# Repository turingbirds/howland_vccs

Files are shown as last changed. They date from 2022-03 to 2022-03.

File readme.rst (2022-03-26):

Practical Measurement of Voltage-Controlled Current Source Output Impedance for Applications in Transcranial Electrical Stimulation
===================================================================================================================================

Welcome to the repository accompanying the conference paper:

    \C\. Linssen and P. Harpe, "Practical Measurement of Voltage-Controlled Current Source Output Impedance for Applications in Transcranial Electrical Stimulation," 2021 IEEE Biomedical Circuits and Systems Conference (BioCAS), 6–9 Oct 2021, pp. 1–6, doi: `10.1109/BioCAS49922.2021.9644974 <https://doi.org/10.1109/BioCAS49922.2021.9644974>`_.

For BibTeX and other citation formats, please visit https://ieeexplore.ieee.org/document/9644974.

This repository contains the simulations, analysis and plotting scripts, prototype PCB designs and empirical measurement data for reproducing the figures in the paper.

The final paper can be downloaded from https://ieeexplore.ieee.org/document/9644974. The IEEE policy permits (`IEEE Publication Services and Products Board Operations Manual 2021, Section 8.1.9 <https://pspb.ieee.org/images/files/files/opsmanual.pdf>`_) authors to disseminate 'preprint' versions of their papers. This 'author preprint version' can be found under `paper/ <paper>`_ and corresponds to the peer-reviewed manuscript submitted as the final version to the conference.

The unabridged preprint, which was *not peer reviewed*, contains additional background information such a loop stability simulations, that could be helpful in reproducing and iterating upon the results in the paper. This unabridged version can be found under the directory `preprint/ <preprint>`_.

We (the authors of the paper) welcome feedback; please write to the corresponding author at c.linssen@donders.ru.nl.

License
-------

Copyright on the paper (figures, text) is held by IEEE (2021):

*© 2021 IEEE. Personal use of this material is permitted. Permission
from IEEE must be obtained for all other uses, in any current or future
media, including reprinting/republishing this material for advertising or
promotional purposes, creating new collective works, for resale or
redistribution to servers or lists, or reuse of any copyrighted
component of this work in other works.*

All materials on this repository that are not covered by IEEE license or copyright, are Copyright (C) 2021, C. Linssen and P. Harpe, and published here under the Apache License 2.0 license, a copy of which is included in this repository at `apache_license_2.0.txt <apache_license_2.0.txt>`_.

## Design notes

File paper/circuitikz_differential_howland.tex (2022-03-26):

\begin{circuitikz}
	\node [op amp] (opampa) at (0, -3) {} (0, 0);
	\node [op amp, yscale=-1] (opampb) at (0, 3) {} (6, 6);

	\node [ocirc, label=left:$V_{in,neg}$] (Vinpos) at (-3., -3.5) {};
	\node [ocirc, label=left:$V_{in,pos}$] (Vinneg) at (-3., 3.5) {};
	\node [circ, label=left:\raisebox{-0.9cm}{$V_{a,neg}$}] (VAneg) at (1.75, .75) {};
	\node [circ, label=left:\raisebox{0.8cm}{$V_{b,neg}$}] (VBneg) at (1.75, -.75) {};
	\node (VAneg2) at (4, -.75) {};
	\node (VBneg2) at (4, .75) {};
	\node [label=above:$V_a$] (VA) at (1.75, 3.) {};
	\node [label=below:$V_b$] (VB) at (1.75, -3.) {};

	\node (VLposint) at (4., 3.) {};
	\node (VLnegint) at (4., -3.) {};
	\node [] (von2) at (4.75, -0.75) {};
	\node [label=above:$V_{L,pos}$] (vlpos) at (6.75, 3) {};
	\node [label=below:$V_{L,neg}$] (vlneg) at (6.75, -3) {};

	\draw (VB.center) to [R, l^=$R_{4b}$, *-*] (VLnegint.center) {};
	\draw (VA.center) to [R, l^=$R_{2b}$, *-*] (VLposint.center) {};

	\draw (Vinpos.center) to [o-] (opampa.+) {};
	\draw (Vinneg.center) to [o-] (opampb.+) {};

	\draw (opampb.-) |- (VAneg) {};
	\draw (opampa.-) |- (VBneg) {};
	\draw (opampa.out) -- (VB.center) {};
	\draw (opampb.out) -- (VA.center) {};
	\draw (VAneg.center) -- (VAneg2.center) to [R, label=$R_{4a}$] (VLnegint.center) {};
	\draw (VLposint.center) to [R, label=$R_{2a}$] (VBneg2.center) -- (VBneg.center) {};
	\draw (VBneg.center) to [R, l=$R_3$] (VB.center) {};
	\draw (VA.center) to [R, l=$R_1$] (VAneg.center) {};

	\draw (VLposint.center) -- (vlpos.center) to [generic, l=$Z_L$, i>^=$I_L$, o-o] (vlneg.center) -- (VLnegint.center) {};
\end{circuitikz}

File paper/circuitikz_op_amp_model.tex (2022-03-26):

\begin{circuitikz}
	\node [label=left:$V_{in,pos}$] (Vinpos) at (-7, -1) {};
	\node [label=left:$V_{in,neg}$] (Vinneg) at (-7, 1) {};
	\node [] (op_vin_p) at (-5.5, -1) {};
	\node [] (op_vin_n) at (-5.5, 1) {};
	\node [] (op_vin_p2) at (-4, -1) {};
	\node [] (op_vin_n2) at (-4, 1) {};

	\draw (Vinneg.center) to [short, o-*] (op_vin_n.center) {};
	\draw (Vinpos.center) to [short, o-*] (op_vin_p.center) {};
	\draw (op_vin_p.center) to [R, l=$R_{in}$] (op_vin_n.center) {};

	\draw (op_vin_n.center) to [short] (op_vin_n2.center) {};
	\draw (op_vin_p.center) to [short] (op_vin_p2.center) {};
	\draw (op_vin_p2.center) to [C, l=$C_{in}$] (op_vin_n2.center) {};

	%
	% 	RC poles: box
	%

	\node [] (vboxtr) at (3, 2) {};
	\node [] (vboxbr) at (3, -2) {};
	\node [] (vboxtl) at (-3, 2) {};
	\node [] (vboxbl) at (-3, -2) {};

	\draw[dashed] (vboxtr.center) to [short] (vboxbr.center) {};
	\draw[dashed] (vboxbr.center) to [short] (vboxbl.center) {};
	\draw[dashed] (vboxbl.center) to [short] (vboxtl.center) {};
	\draw[dashed] (vboxtl.center) to [short] (vboxtr.center) {};

	%
	% 	RC poles
	%

	\node [] (gainshaping_gt) at (-1.5, 1) {};
	\node [] (gainshaping_gb) at (-1.5, -1) {};
	\node [label=above:$V_{n}$] (gainshaping_rt) at (0, 1) {};
	\node [] (gainshaping_rb) at (0, -1) {};
	\node [] (gainshaping_ct) at (1.5, 1) {};
	\node [] (gainshaping_cb) at (1.5, -1) {};
	\draw (gainshaping_gb.center) to [american controlled current source, l=$g_{n}$] (gainshaping_gt.center) {};
	\draw (gainshaping_gb.center) to [short, *-] ++(0, -.2) node [rground] {};
	\draw (gainshaping_rt.center) to [R, l=$R_{n}$, *-*] (gainshaping_rb.center) {};
	\draw (gainshaping_ct.center) to [C, l=$C_{n}$] (gainshaping_cb.center) {};
	\draw (gainshaping_gt.center) to [short] (gainshaping_rt.center) {};
	\draw (gainshaping_rt.center) to [short] (gainshaping_ct.center) {};
	\draw (gainshaping_gb.center) to [short] (gainshaping_rb.center) {};
	\draw (gainshaping_rb.center) to [short] (gainshaping_cb.center) {};

	%
	% 	the output VCVS and output resistance
	%

	\node [] (v1t) at (4, 1) {};
	\node [] (v1b) at (4, -1) {};
	\node [label=right:$V_{out}$] (f1bp) at (7, 1) {};
	\draw (v1t.center) to [american controlled voltage source, l=$E_{out}$] (v1b.center) {};
	\draw (v1t.center) to [R, l=$R_{out}$, -o] (f1bp.center) {};
	\draw (v1b.center) to [short] ++(0, -.2) node [rground] {};
\end{circuitikz}

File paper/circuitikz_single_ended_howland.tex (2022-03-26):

\begin{circuitikz}

	\node [op amp] (opamp) {} (0,0);

	\node [label=left:$V_{in,pos}$] (Vinpos) at (-6, -2) {};
	\node [label=left:$V_{in,neg}$] (Vinneg) at (-6, 2) {};
	\node [label=below:$V_{pos}$] (op_vp) at (-2, -2) {};
	\node [label=above:$V_{neg}$] (op_vn) at (-2, 2) {};
	\node [label=right:$V_L$] (vb) at (2, -2) {};
	\node [label=right:$V_o$] (va) at (2, 0) {};
	\node [] (vdummy) at (2, -2.5) {};

	\draw (vb.center)+(0, -0.2) to [generic, l=$Z_L$, i>^=$I_L$] +(0, -2.2) node [rground] at +(0, -2) {};
	\draw (opamp.out) -- (va.center) {};

	\draw (Vinneg.center) to [R, l=$R_1$, o-*] (op_vn.center) {};
	\draw (Vinpos.center) to [R, l=$R_3$, o-*] (op_vp.center) {};
	\draw (op_vp.center) to [R, l=$R_{4a}$] (vb.center) {};
	\draw (va.center) |- (2, 2) to [R, l_=$R_2$] (op_vn.center) {};
	\draw (vb.center) -- (vdummy.center) {};

	\draw (opamp.+) -| (-2, -2) to (op_vp.center) {};
	\draw (opamp.-) -| (-2, 2) to (op_vn.center) {};

	\draw (va) to [R, l^=$R_{4b}$, *-o] (vb) {};
\end{circuitikz}

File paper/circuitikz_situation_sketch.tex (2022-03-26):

\begin{circuitikz}
	\node [] (topleft) at (-1, 1) {};
	\node [] (bottomleft) at (-1, -1) {};

	\node [] (topright) at (2, 1) {};
	\node [] (bottomright) at (2, -1) {};

	\node [] (topright1) at (4, 1) {};
	\node [] (bottomright1) at (4, -1) {};

	\node [] (topright2) at (5, 1) {};
	\node [] (bottomright2) at (5, -1) {};

	\draw (topleft.center) to [generic, l=$Z_L$]  (bottomleft.center) {};
	\draw (bottomright1.center) to [generic, l=$Z_{out}$, *-*]  (topright1.center) {};
	\draw (bottomright2.center) to [american controlled current source, l_=$g_m$]  (topright2.center) {};
	\draw (topleft.center) to [generic, l=$Z_{elec}$, i<^=$I_L$]  (topright.center) {};
	\draw (bottomleft.center) to [generic, l=$Z_{elec}$]  (bottomright.center) {};
	\draw (topright.center) to [short] (topright1.center) {};
	\draw (bottomright.center) to [short] (bottomright1.center) {};
	\draw (topright1.center) to [short] (topright2.center) {};
	\draw (bottomright1.center) to [short] (bottomright2.center) {};

	%
	% 	RC poles: box
	%

	\node [] (vboxtr) at (2.75, 1.4) {};
	\node [] (vboxbr) at (2.75, -1.4) {};
	\node [] (vboxtl) at (6.25, 1.4) {};
	\node [] (vboxbl) at (6.25, -1.4) {};

	\draw[dashed] (vboxtr.center) to [short] (vboxbr.center) {};
	\draw[dashed] (vboxbr.center) to [short] (vboxbl.center) {};
	\draw[dashed] (vboxbl.center) to [short] (vboxtl.center) {};
	\draw[dashed] (vboxtl.center) to [short] (vboxtr.center) {};
\end{circuitikz}

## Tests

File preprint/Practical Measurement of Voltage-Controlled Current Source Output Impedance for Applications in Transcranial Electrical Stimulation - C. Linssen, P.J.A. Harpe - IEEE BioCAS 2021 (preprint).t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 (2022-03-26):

\documentclass[10pt]{article}

\addtolength{\topmargin}{-.5in}
\addtolength{\textheight}{1in}

\usepackage{amsmath}
\let\OldAngle\angle
\renewcommand{\angle}{\anglesym}

\usepackage{rotating}
\usepackage{graphicx}
\graphicspath{{figures/}}

\usepackage{epstopdf}
\epstopdfsetup{outdir=./}

\usepackage{natbib}
\bibpunct{[}{]}{;}{n}{,}{,} % required for natbib

\usepackage{multirow,tabularx}
% \usepackage{SIunits}
\usepackage{xspace}
\usepackage[table]{xcolor}% http://ctan.org/pkg/xcolor

\usepackage{hyperref}
\usepackage{hypcap} % Correct a problem with hyperref

\usepackage{circuitikz}
\usetikzlibrary{arrows}
\usepackage[justification=raggedright,font=small]{caption}
\usepackage{subcaption}

\usepackage{mathpazo}
\usepackage{lmodern,textcomp}

\usepackage{tcolorbox}% http://ctan.org/pkg/tcolorbox

\usepackage[free-standing-units]{siunitx}
\usepackage{cleveref}% load last

% \sisetup{math-degree=\mbox{\textdegree},text-degree=\textdegree}
% \sisetup{math-celsius=\mbox{\textdegree}C,text-celsius=\textdegree C}

\usepackage{mathtools}

\crefname{equation}{equation}{eq. }
\Crefname{equation}{Eq.}{Eq.}% For beginning \Cref
\crefrangelabelformat{equation}{(#3#1#4--#5#2#6)}

\crefmultiformat{equation}{eq. #2#1#3}{, #2#1#3}{#2#1#3}{#2#1#3}
\Crefmultiformat{equation}{Eq. #2#1#3}{, #2#1#3}{#2#1#3}{#2#1#3}

%\usepackage{pdfcomment}

% PDFCOMMENT EXAMPLES:

% You can do much more \pdfmarkupcomment[markup=Squiggly,color=green,author=CAP]{with pdfcomment}{move to the front}.
% This is a \pdfmarkupcomment[markup=StrikeOut,color=red,author=CAP]{stupid}{replace stupid with funny}  game!
% \pdfmarkupcomment[markup=Highlight,color=yellow,author=CAP]{Of course, you can highlight complete sentences.}{Highlight}
% This is very\pdfcomment[icon=Note,color=blue]{insert graphic!} interesting!

\newcommand{\specialcell}[2][c]{%
  \begin{tabular}[#1]{@{}l@{}}#2\end{tabular}}

\newcommand\redbox[3][red]{\textcolor{#1}{\rule{#2}{#3}}}

\newcommand{\brieftbllink}[1]{\hyperref[#1]{Tbl.~\ref*{#1}}\xspace }
\newcommand{\briefeqlink}[1]{\hyperref[#1]{Eq.~\ref*{#1}}\xspace }
\newcommand{\tablelink}[1]{\hyperref[#1]{Tbl.~\ref*{#1}}\xspace }
\newcommand{\eqlink}[1]{\hyperref[#1]{Equation~\ref*{#1}}\xspace }
\newcommand{\briefseclink}[1]{\hyperref[#1]{Sec.~\ref*{#1}}}
\newcommand{\briefappxlink}[1]{\hyperref[#1]{App.~\ref*{#1}}}
\newcommand{\seclink}[1]{\hyperref[#1]{Section~\ref*{#1}}}
\newcommand{\parbreak}{\ \\
\noindent}
\newcommand{\brieffiglink}[1]{\hyperref[#1]{Fig.~\ref*{#1}}}
\newcommand{\brieffigsublink}[2]{\hyperref[#1]{Fig.~\ref*{#1}#2}}

\newcommand{\vulgaronehalf}{${}^1\!\!\mskip0.3\thinmuskip/\!{}_2$}

\def\changemargin#1#2{\list{}{\rightmargin#2\leftmargin#1}\item[]}
\let\endchangemargin=\endlist 

\title{Practical Measurement of Voltage-Controlled Current Source Output Impedance for Applications in Transcranial Electrical Stimulation\\[.5cm]\colorbox{yellow!30}{\emph{Unabridged preprint}}\\[.1cm]\colorbox{yellow!30}{\small For the original paper and citation, please see Appendix}}

\author{Charl Linssen\\
\small Donders Institute for Brain, Cognition and Behaviour\\
\small Radboud University\\
\small Nijmegen, The Netherlands\\
\small \texttt{<c.linssen@donders.ru.nl>}\\[0.5cm]
Pieter Harpe\\
\small Integrated Circuits Group\\
\small Eindhoven University of Technology\\
\small Eindhoven, The Netherlands\\
\small \texttt{<p.j.a.harpe@tue.nl>}\\[0.5cm]
\date{\today}
}

%%%%%%%%%%%%%%%%%%%%%%%%%%%%%%%%%%%%%%%%%%%%%%%%%%%%%%%%%%%%%%%%%%%%%%%%%%%%%%
%%%%%%%%%%%%%%%%%%%%%%%%%%%%%%%%%%%%%%%%%%%%%%%%%%%%%%%%%%%%%%%%%%%%%%%%%%%%%%
\begin{document}

\maketitle

%%%%%%%%%%%%%%%%%%%%%%%%%%%%%%%%%%%%%%%%%%%%%%%%%%%%%%%%%%%%%%%%%%%%%%%%%%%%%%
%%%%%%%%%%%%%%%%%%%%%%%%%%%%%%%%%%%%%%%%%%%%%%%%%%%%%%%%%%%%%%%%%%%%%%%%%%%%%%
\begin{abstract}
\noindent A voltage-controlled current source (VCCS) is a key component in the electrical stimulation of neuronal tissue. We present a method for the evaluation of output impedance across frequency, of VCCS circuits with applications in transcranial electrical stimulation (tES). Two VCCS circuit architectures, one with a single-ended, and one with a differential output, are theoretically analysed and simulated, and the method is validated by matching these results with empirical measurements. Monte Carlo simulation of the measurement method itself is used to predict its range of applicability under real-world conditions. Both circuits, as well as the method used to determine output impedance, are easy to reproduce, using generic hardware components at low cost. The method described has immediate practical application value in neuroscience research, where it can be used in the deployment and further development of VCCS circuit architectures.
\end{abstract}

\tableofcontents

%%%%%%%%%%%%%%%%%%%%%%%%%%%%%%%%%%%%%%%%%%%%%%%%%%%%%%%%%%%%%%%%%%%%%%%%%%%%%%
\section{Motivation}
\label{sec:motivation}
%%%%%%%%%%%%%%%%%%%%%%%%%%%%%%%%%%%%%%%%%%%%%%%%%%%%%%%%%%%%%%%%%%%%%%%%%%%%%%

Transcranial electrical stimulation (tES) is a relatively non-invasive way of altering the excitability of the brain. A direct, alternating or noise current (tDCS, tACS or tRNS, respectively) is delivered between two electrodes that have been placed into conductive contact with the subject's skin, on or near the scalp (\brieffiglink{fig:situation_sketch}, top). Bandwidth of the stimulation is typically below $1~\kilo\hertz$ and currents are below $2~\milli\ampere$ \cite{pmid26652115}\cite{pmid19109497}. In addition to tES, voltage-controlled current sources are key components in other stimulation methods of the nervous system, such as Deep Brain Stimulation (DBS), where similar operating parameters are required \cite{dbs}.

\begin{figure}[bt]
	\begin{subfigure}{\textwidth}
        \centering
\makebox[\textwidth][c]{%
		
        % \caption{\small abc}
        }
        \caption{}
        \label{fig:situation_sketch1}
    \end{subfigure}

	\begin{subfigure}{\textwidth}
        \centering
\makebox[\textwidth][c]{%
\input{../paper/circuitikz_situation_sketch.tex}
}
        \caption*{\small}
        \label{fig:situation_sketch2}
    \end{subfigure}
\caption{\small Situation sketch (top panel) and equivalent circuit (bottom panel). In a typical tES session, the device is adjusted to supply a given current $I_L$ into a load $Z_L$ via two electrodes, each with interfacial impedance $Z_{elec}$. We assume the device is battery powered or in any case galvanically isolated; the ground node is thus elided in the bottom panel.}
\label{fig:situation_sketch}
\end{figure}

There is a trend towards smaller electrodes in tES, which allow for controlling the stimulation at a higher spatial resolution \cite{pmid23031743}. Smaller electrodes have a higher electrode (electrode/electrolyte, or interfacial) impedance (\brieffiglink{fig:situation_sketch}, bottom), and thus in general need higher drive voltages to maintain the same current. Drive voltages can also be paradoxically high, even with common tES electrode sizes (on the order of $50~\centi\meter^2$), for especially \emph{low} currents. For tDCS at $2.5~\milli\ampere$, an extrapolated voltage swing of at least $18.3~\volt$ is required from the VCCS, ``for the top 99th percentile'' of subjects \cite{pmid25018056}; \cite{pmid20488204} report using values as high as $66.7~\volt$.

To obtain larger output voltage swing, a VCCS with a differential output can be used. In a single-ended architecture, one of the electrodes is connected to ground, while the other is driven by the VCCS. In a differential design, instead, both sides are actively driven by the VCCS. This requires twice as many amplifiers or output drivers, but results in an effective doubling of the output voltage range when one side of the load is driven in antiphase with the other. Further benefits include an improved signal bandwidth, immunity to changes in the load, and noise immunity \cite{pmid24880419}.

Here, we present a universal, low-cost method to measure VCCS output impedance, to guide the design and empirical performance validation of any single-ended or differential output current source, in the operating regime that is typical for tES with human subjects. To improve the interpretability of obtained results, we selected two related circuits for evaluation, so that results may be compared on a relative basis. Each of these circuits is a variant of the well-known ``improved Howland'' current source, which can be built using commodity, off-the-shelf parts with low total cost, excellent performance, and large output voltage swing \cite{Franco1988}. Howland sources require precise matching of resistor values to obtain good performance, which can be adequately addressed by trimming using a single potentiometer (or two in the case of the differential source). These features make them an excellent alternative to custom silicon where access to tooling, turnaround time, customisation or cost are of concern.

We begin with a mathematical analysis (\briefseclink{sec:analysis}) and simulation studies (\briefseclink{sec:sim_results}), continue with empirical measurements (\briefseclink{sec:empirical-results}), and conclude in \briefseclink{sec:conclusion}.

\raggedbottom

%%%%%%%%%%%%%%%%%%%%%%%%%%%%%%%%%%%%%%%%%%%%%%%%%%%%%%%%%%%%%%%%%%%%%%%%%%%%%%
\section{Previous work}
\label{sec:previous_work}
%%%%%%%%%%%%%%%%%%%%%%%%%%%%%%%%%%%%%%%%%%%%%%%%%%%%%%%%%%%%%%%%%%%%%%%%%%%%%%

A straightforward differential version of the Howland current source uses two of the exact same single-ended Howland current sources, one to drive the anode and one to drive the cathode. A common drive signal (the voltage indicating current setpoint) is connected to the positive-phase input of the anodal VCCS and the negative-phase input of the cathodal VCCS \cite{1742-6596-407-1-012030}\cite{pmid19706961}. This configuration relies on the non-ideal (finite) output resistance of each current source to balance the two legs of the circuit, making it extremely sensitive to small variations in component values, causing an unacceptably large common-mode voltage.

A potential solution to the problem of imbalance is to use an active feedback circuit that nulls the common-mode voltage at the output \cite{US2002060915A1:misc}. This prevents one of the legs from floating to the supply rail. A disadvantage of this circuit is the large number of components used (7 op-amps and 14 precision resistors) and required matching.

The differential source in \cite{pmid24880419} is based on the single-ended improved Howland, but extends the circuit by two op-amps. A single-ended Howland source drives the anodal leg of the circuit as normal. A new pair of op-amps, configured as an inverting voltage follower, drive the cathode voltage to be equal and opposite to the anode voltage. This architecture was found to perform well in comparison to a normal, single-ended configuration, approximately doubling the differential output impedance over a wide frequeny range. This design shows a differential but not symmetric output, which could affect noise rejection to external interference, because the cathode terminal output impedance will be different from the anode terminal output impedance. Frequency compensation of the voltage follower can introduce additional instabilities.

Another family of circuits is based around the use of a fully differential output op-amp \cite{offsetfree_bidirectional_current_source}\cite{SirtoliMorcellesVincence}, which have the advantage of very small common-mode output voltage.

A fully differential circuit similar to the improved Howland was described in \cite{simmonds2009differential}. One op-amp is connected to the anode of the load through a sense resistor, and a second op-amp connects to the cathode through a second sense resistor. The net negative feedback to one op-amp is then given by the voltage drop over the sense resistor on the opposite leg. This circuit is fully symmetrical and requires only two standard op-amps and six precision resistors. In the remainder of this paper, we use this circuit as a benchmark.

%%%%%%%%%%%%%%%%%%%%%%%%%%%%%%%%%%%%%%%%%%%%%%%%%%%%%%%%%%%%%%%%%%%%%%%%%%%%%%
%%%%%%%%%%%%%%%%%%%%%%%%%%%%%%%%%%%%%%%%%%%%%%%%%%%%%%%%%%%%%%%%%%%%%%%%%%%%%%
\section{Analysis}
\label{sec:analysis}
%%%%%%%%%%%%%%%%%%%%%%%%%%%%%%%%%%%%%%%%%%%%%%%%%%%%%%%%%%%%%%%%%%%%%%%%%%%%%%

Throughout the analysis and results sections, we compare a single-ended with a differential VCCS using a common set of measurements. This allows us to distinguish the relative performance gained by changing to a differential architecture from the absolute performance, which is affected by implementation details such as selection of the op-amp IC.

In this section, we analytically determine the gain, compliance voltage and predicted output resistance for the single-ended version, followed by the differential circuit. Derivations were carried out with the help of Wolfram Mathematica \cite{mathematica}.

%%%%%%%%%%%%%%%%%%%%%%%%%%%%%%%%%%%%%%%%%%%%%%%%%%%%%%%%%%%%%%%%%%%%%%%%%%%%%%
\subsection{Single-ended ``improved'' Howland VCCS}
\label{sec:single_ended_howland}

The improved Howland circuit is based on a standard op-amp and five precision resistors. It is a single-ended circuit, meaning one side of the load is connected to ground (\brieffiglink{fig:single_ended_howland}). The operation of the circuit can be understood as follows: there is both negative feedback (via $R_2$) and positive feedback (via $R_{4a}$). The difference between positive and negative feedback is proportional to the load current (via the ratio $R_2/R_{4b}$). No current flows into the input terminals of the op-amp, so the same difference in current exists between $R_1$ and $R_3$. But as $V_{pos}=V_{neg}$ in normal operation, these currents are in turn proportional to the input voltage $V_{in,pos}-V_{in,neg}$. Thus, overall, the load current is proportional to the input voltage.

%%%%%%%%%%%%%%%%%%%%%%%%%%%%%%%%%%%%%%%%%%%%%%%%%%%%%%%%%%%%%%%%%%%%%%%%%%%%%%
\subsubsection{DC analysis}

\begin{figure}
\centering
\input{../paper/circuitikz_single_ended_howland.tex}
\caption{\small Circuit diagram of the single-ended ``improved'' Howland source. $Z_L$ is the load impedance external to the VCCS.}
\label{fig:single_ended_howland}
\end{figure}

Let $A_{OL}$ be the (finite) gain of the op-amp. The input-output relationship of the op-amp can be written as
\begin{subequations}
\label{eq:prerequisites}
\begin{gather}
\label{eq:finite_gain_opamp}
V_o = A_{OL}\cdot(V_{pos}-V_{neg})\\
\intertext{To derive the gain of the VCCS, we start by applying Kirchhoff's Current Law (KCL) to node $V_{pos}$ and $V_{neg}$:}
\label{eq:finite_gain_opamp2}
\frac{V_{in,pos}-V_{pos}}{R_3} - \frac{V_{pos} - V_L}{R_{4a}}=0\\
\frac{V_o - V_{neg}}{R_2} - \frac{V_{neg} - V_{in,neg}}{R_1}=0\\
\intertext{Similarly we apply KCL to the output node $V_L$:}
\frac{V_o-V_L}{R_{4b}} + \frac{V_{pos}-V_L}{R_{4a}} - I_L = 0\label{eq:se_1}
\end{gather}
\end{subequations}
For a given load $Z_L$, and assuming $A_{OL}=\infty$, combining \briefeqlink{eq:finite_gain_opamp}---\briefeqlink{eq:se_1} yields the transfer function of the VCCS:
\begin{align}
\label{eq:single_ended_howland_transfer_function}
\frac{I_L}{V_{in,diff}} = \frac{1}{2}\cdot\frac{R_2 (R_3 + 2 R_{4a}) + R_1(R_{4a} + R_{4b})}{R_2 R_3 Z_L - R_1 (R_3 R_{4b} + R_{4b} Z_L + R_{4a} (R_{4b} + Z_L))}
\end{align}
with $V_{in,diff}=V_{in,pos}-V_{in,neg}$. Under the conditions that
\begin{subequations}
\label{eq:single_ended_howland_conditions}
\begin{align}
A_{OL} &= \infty\\
R_1 &= R_3\label{eq:single_ended_howland_conditions_r1}\\
R_2 &= R_{4a} + R_{4b}\label{eq:single_ended_howland_conditions_r2}
\end{align}
\end{subequations}
\briefeqlink{eq:finite_gain_opamp}---\briefeqlink{eq:se_1} simplify such that the output current does not depend on output voltage (i.e. the $V_L$-dependent term vanishes). The transfer function can then be written as:
\begin{subequations}
\label{eq:single_ended_gain}
\begin{equation}
I_L = g_m\cdot V_{in,diff}
\end{equation}
with
\begin{equation}
g_m = \frac{R_2}{R_3R_{4b}}
\end{equation}
\end{subequations}
the transconductance of the VCCS in units of Amp\`{e}re per Volt.

%%%%%%%%%%%%%%%%%%%%%%%%%%%%%%%%%%%%%%%%%%%%%%%%%%%%%%%%%%%%%%%%%%%%%%%%%%%%%%
\subsubsection{Output resistance}
\label{sec:singla_ended_output_resistance}

Ideally, the output resistance of a VCCS is infinite. In practice, it attains only a finite value, due to limitations of the op-amp, and imperfect matching of the resistors (violations of \briefeqlink{eq:single_ended_howland_conditions} and \briefeqlink{eq:diff_howland_conditions}). An expression for output impedance can be obtained by taking the partial differential of the output voltage with respect to the output current:
\begin{align}
\label{eq:rout_single_ended}
Z_{out} &= \frac{\partial V_L}{\partial{}I_L}\nonumber\\
&= -\frac{\alpha + A_{OL}\cdot\beta}{\gamma + A_{OL}\cdot\delta}
\end{align}
with
\begin{align}
\alpha &= (R_1 + R_2) (R_3 + R_{4a}) R_{4b}\nonumber\\
\beta &= R_1 (R_3 + R_{4a}) R_{4b}\nonumber\\
\gamma &= (R_1 + R_2) (R_3 + R_{4a} + R_{4b})\nonumber\\
\delta &= R_1 (R_{4a} + R_{4b}) - R_2 R_3\nonumber
\end{align}
which is indeed infinite under the conditions given by \briefeqlink{eq:single_ended_howland_conditions}.

Note that for certain combinations of values, the output resistance can exhibit a negative sign. In this case, load current will increase with increasing load resistance. Intuitively, it is a consequence of the positive feedback in the circuit (via $R_{4a}$) being too strong with respect to the negative feedback (via $R_2$). This situation, where positive feedback dominates, could theoretically cause instability. The magnitude of the effect is in the form of a transconductance with magnitude (``differential gain'') equal to $1/|Z_{out}|$. Thus, for a circuit where the resistors are reasonably well matched, $Z_{out}$ is very high and this gain is infinitessimal.

%  if the load exhibits a nonlinearity, for example, if $R_L$ itself decreases with voltage $V_L$.

%%%%%%%%%%%%%%%%%%%%%%%%%%%%%%%%%%%%%%%%%%%%%%%%%%%%%%%%%%%%%%%%%%%%%%%%%%%%%%
\subsubsection{Compliance voltage}
\label{sec:single_ended_compliance_voltage}

The compliance voltage (maximum output voltage span) is in practice limited by the saturation voltage of the op-amp $V_{sat,pp}$ (e.g. $28~\volt$ for a $\pm15~\volt$ op-amp), and the voltage drop across the series resistor $R_{4b}$ caused by $I_L$, while the contribution of the positive feedback path (through $R_{4a}$) is negligible:

\begin{align}
\label{eq:single_ended_compliance_voltage}
|V_L|\leq V_{sat,pp} - R_{4b}|I_{L,max}|
\end{align}
To obtain the largest output voltage swing, $R_{4b}$ should be chosen as small as possible, taking other constraints on the circuit into account.

\begin{figure}[tb]
\centering
\noindent\makebox[\textwidth]{%
\input{../paper/circuitikz_differential_howland.tex}
}
\caption{\small Circuit diagram of the fully differental ``improved'' Howland source. $Z_L$ is the load impedance external to the VCCS.}
\label{fig:differential_howland}
\end{figure}

%%%%%%%%%%%%%%%%%%%%%%%%%%%%%%%%%%%%%%%%%%%%%%%%%%%%%%%%%%%%%%%%%%%%%%%%%%%%%%%
%%%%%%%%%%%%%%%%%%%%%%%%%%%%%%%%%%%%%%%%%%%%%%%%%%%%%%%%%%%%%%%%%%%%%%%%%%%%%%%
\subsection{Differential version of the ``improved'' Howland VCCS}
\label{sec:differential_howland}

To actively drive both sides of the load, the differential version uses two op-amps and six precision resistors (\brieffiglink{fig:differential_howland}). It operates in a manner analogous to the single-ended version, the voltages in the bottom half having equal magnitude but opposite sign from the top half at all times. For each of the halves, the positive part of the feedback is now obtained via the negative input terminal of the op-amp. This is achieved by obtaining the feedback voltage from the other side of the circuit, where it has an inverted sign (this is the X-shaped crossing in the circuit). $R_1$ and $R_3$ in the differential circuit are analog to $R_2$ in the single-ended version, conveying negative feedback. $R_{2a}$ and $R_{4a}$ are analogous to $R_{4a}$ in the single-ended circuit and convey what is effectively positive feedback because of the sign inversion.

%%%%%%%%%%%%%%%%%%%%%%%%%%%%%%%%%%%%%%%%%%%%%%%%%%%%%%%%%%%%%%%%%%%%%%%%%%%%%%%
\subsubsection{DC analysis}

Starting again with the definition of an op-amp with finite gain $A_{OL}$:
\begin{subequations}
\label{eq:diff_1}
\begin{gather}
V_a = A_{OL}\cdot(V_{in,pos} - V_{a,neg})\\
V_b = A_{OL}\cdot(V_{in,neg} - V_{b,neg})
\end{gather}
\end{subequations}
Apply KCL to nodes $V_{L,pos}$ and $V_{L,neg}$:
\begin{subequations}
\label{eq:diff_2}
\begin{gather}
\frac{V_a - V_{L,pos}}{R_{2b}} - \frac{V_{L,pos} - V_{b,neg}}{R_{2a}} - I_L = 0\\
\frac{V_b - V_{L,neg}}{R_{4b}} - \frac{V_{L,neg} - V_{a,neg}}{R_{4a}} + I_L = 0
\end{gather}
\end{subequations}
Apply KCL to nodes $V_{a,neg}$ and $V_{b,neg}$:
\begin{subequations}
\label{eq:diff_3}
\begin{gather}
\frac{V_a - V_{a,neg}}{R_1} + \frac{V_{L,neg} - V_{a,neg}}{R_{4a}} = 0\\
\frac{V_b - V_{b,neg}}{R_3} + \frac{V_{L,pos} - V_{b,neg}}{R_{2a}} = 0
\end{gather}
\end{subequations}
In addition, we use the auxilary equation for the differential output voltage $V_L$:
\begin{equation}
\label{eq:diff_4}
V_L = V_{L,pos} - V_{L,neg}
\end{equation}
For a given load $Z_L$, and assuming $A_{OL}=\infty$, combining \briefeqlink{eq:diff_1}--\briefeqlink{eq:diff_4} yields the transfer function:
\begin{align}
\label{eq:diff_howland_transfer_function}
\frac{I_L}{V_{in,diff}} = \frac{R_1 (R_{2a} + R_3) + R_{4a} (R_{2a} + R_3) - R_{2b} R_{4b} }{ \left( \begin{aligned}&Z_L((R_{2a} + R_{2b})(R_{4a} + R_{4b}) - R_1 R_3)\\&+ R_{2a}(R_{4b}(R_1 + R_{4a}) + R_{2b}(R_{4a}+R_{4b}))\\&+ R_{2b}R_{4a}(R_3+R_{4b})\end{aligned}\right)}
\end{align}
Under the conditions that
\begin{subequations}
\label{eq:diff_howland_conditions}
\begin{align}
R_{2b} &= R_{4b}\\
R_{2a} &= R_{4a}\\
R_1 = R_3 &= R_{2b} + R_{2a}\\
V_{in,pos} &= -V_{in,neg}
\end{align}
\end{subequations}
\briefeqlink{eq:diff_1}--\briefeqlink{eq:diff_4} simplify such that the output current does not depend on output voltage (i.e. the $V_L$ term vanishes). The transfer function can then be written as:
\begin{subequations}
\label{eq:diff_gain}
\begin{equation}
I_L = g_m \cdot V_{in,diff}
\end{equation}
with
\begin{equation}
g_m = \frac{1}{R_{2b}}
\end{equation}
\end{subequations}

%%%%%%%%%%%%%%%%%%%%%%%%%%%%%%%%%%%%%%%%%%%%%%%%%%%%%%%%%%%%%%%%%%%%%%%%%%%%%%%
\subsubsection{Compliance voltage}

The main limiting factor of the compliance voltage is, as before, the saturation voltage of the op-amp, and secondly, the voltage drop across (in this case not one but two) resistors $R_{2b}$ and $R_{4b}$ (with $R_{2b}=R_{4b}$). If resistor values are chosen to be equal (see \tablelink{tbl:resistor_vales}), this yields a compliance voltage twice that of the single-ended variant:
\begin{align}
\label{eq:diff_compliance_voltage}
|V_L|\leq 2\left(V_{sat,pp} - R_{2b}|I_{L,max}|\right)
\end{align}

%%%%%%%%%%%%%%%%%%%%%%%%%%%%%%%%%%%%%%%%%%%%%%%%%%%%%%%%%%%%%%%%%%%%%%%%%%%%%%%
\subsubsection{Output resistance}
\label{sec:symmetrical_vccs_output_resistance}
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

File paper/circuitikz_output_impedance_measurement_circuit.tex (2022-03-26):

\begin{circuitikz}
	\node [op amp] (opamp) at (7.5, 1.49) {} ;
	\node [spdt, rotate=270, yscale=-1] (spdt) at (5.3, .4) {} ;

    \node [] (VLpos) at (4, -2.2) {};
% 	\node [label=right:$V_{L,pos}$] (VLneg) at (8, 2) {};
	\node [] (VLneg) at (8, 2) {};
	\node [] (VLnegmeas) at (12, 2) {};
	\node [] (op_vin_p) at (2, -2.2) {};
	\node [] (op_vin_n) at (2, 2) {};
	\node [] (op_vin_p2) at (1, -2.2) {};
	\node [] (op_vin_n2) at (1, 2) {};

	\node [] (vboxtr) at (-2., 1.4) {};
	\node [] (vboxbr) at (-2., -2.6) {};
	\node [] (vboxtl) at (1.5, 1.4) {};
	\node [] (vboxbl) at (1.5, -2.6) {};

	\draw[dashed] (vboxtr.center) to [short] (vboxbr.center) {};
	\draw[dashed] (vboxbr.center) to [short] (vboxbl.center) {};
	\draw[dashed] (vboxbl.center) to [short] (vboxtl.center) {};
	\draw[dashed] (vboxtl.center) to [short] (vboxtr.center) {};

	\draw (-.75, -2.2) to [american controlled current source, l=$g_m$] (-.75, 1) {}; % , i^>=$I$
	\draw (0.25, 1) to [generic, l=$Z_{out}$, *-*] (0.25, -2.2) {};
	\draw (2, 1) to [R, l=$R_{sens}$, i>^=$I_L$, -*] (5.3, 1) {};
	\draw (2, -2.2) to [short] (5.3, -2.2) {};
% 	\draw (2, -2.2) to [R, l=$R_{sens}'$, color=lightgray!50] (5.3, -2.2) {};
	\draw (spdt.out 1)+(0, .2) to [R, a=$R_{L,a}$, -*] +(0, -2) {};
	\draw (spdt.out 2)+(0, .2) to [R, l=$R_{L,b}$] +(0, -2) {};

	\draw (opamp.+) to +(-1, 0) {};
	\draw (opamp.-) -| +(-4.3, 0) to +(-4.3, 0) to [short, -*] (2, 1) {};

	% IA resistor
	\draw (opamp.-)+(0, -.1) to [R, resistors/scale=.5] +(0, -.85) {};
	\draw (opamp.-)+(0, -.1) to +(.35, -.1) {};
	\draw (opamp.-)+(0, -.85) to +(.35, -.85) {};

	% voltmeter
    \draw (opamp.out) -- +(0, 0) to +(0,-.25) to [rmeter, t=\large V] +(0, -1.25) node[rground] {};

 	\draw (5.621, -2.2) to [short] (5, -2.2) {};
	\draw (-.757, -2.2) to [short] (2, -2.2) {};
	\draw (-.757, 1) to [short] (2, 1) {};

% 	\draw (op_vin_n) to [short] (op_vin_n2) {};
% 	\draw (VLneg) to [short] (op_vin_n2) {};
% 	\draw (op_vin_p) to [short] (op_vin_p2) {};
\end{circuitikz}

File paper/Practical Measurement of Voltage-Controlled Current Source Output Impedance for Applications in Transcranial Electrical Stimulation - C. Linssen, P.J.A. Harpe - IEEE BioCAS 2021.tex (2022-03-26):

\documentclass[conference]{IEEEtran}
\IEEEoverridecommandlockouts
% The preceding line is only needed to identify funding in the first footnote. If that is unneeded, please comment it out.
% \usepackage{cite}
\usepackage{amsmath,amssymb,amsfonts}
\let\OldAngle\angle
\renewcommand{\angle}{\anglesym}

\usepackage{rotating}
\usepackage{graphicx}
\usepackage{balance}

\usepackage{epstopdf}
\epstopdfsetup{outdir=./}

\usepackage{natbib}
\bibpunct{[}{]}{;}{n}{,}{,} % required for natbib

\usepackage{multirow,tabularx}
% \usepackage{SIunits}
\usepackage{xspace}
\usepackage[table]{xcolor}% http://ctan.org/pkg/xcolor

\usepackage{hyperref}
\usepackage{hypcap} % Correct a problem with hyperref

\usepackage{circuitikz}
\usetikzlibrary{arrows}
\usepackage[justification=raggedright,font=small]{caption}
\usepackage{subcaption}

\usepackage[free-standing-units]{siunitx}
\usepackage{cleveref}% load last

\usepackage{mathtools}

\crefname{equation}{equation}{eq. }
\Crefname{equation}{Eq.}{Eq.}% For beginning \Cref
\crefrangelabelformat{equation}{(#3#1#4--#5#2#6)}

\crefmultiformat{equation}{eq. #2#1#3}{, #2#1#3}{#2#1#3}{#2#1#3}
\Crefmultiformat{equation}{Eq. #2#1#3}{, #2#1#3}{#2#1#3}{#2#1#3}

%\usepackage{pdfcomment}

% PDFCOMMENT EXAMPLES:

% You can do much more \pdfmarkupcomment[markup=Squiggly,color=green,author=CAP]{with pdfcomment}{move to the front}.
% This is a \pdfmarkupcomment[markup=StrikeOut,color=red,author=CAP]{stupid}{replace stupid with funny}  game!
% \pdfmarkupcomment[markup=Highlight,color=yellow,author=CAP]{Of course, you can highlight complete sentences.}{Highlight}
% This is very\pdfcomment[icon=Note,color=blue]{insert graphic!} interesting!

\newcommand{\specialcell}[2][c]{%
  \begin{tabular}[#1]{@{}l@{}}#2\end{tabular}}

\newcommand\redbox[3][red]{\textcolor{#1}{\rule{#2}{#3}}}

\newcommand{\brieftbllink}[1]{\hyperref[#1]{Tbl.~\ref*{#1}}\xspace }
\newcommand{\briefeqlink}[1]{\hyperref[#1]{Eq.~\ref*{#1}}\xspace }
\newcommand{\tablelink}[1]{\hyperref[#1]{Tbl.~\ref*{#1}}\xspace }
\newcommand{\eqlink}[1]{\hyperref[#1]{Equation~\ref*{#1}}\xspace }
\newcommand{\briefseclink}[1]{\hyperref[#1]{Sec.~\ref*{#1}}}
\newcommand{\seclink}[1]{\hyperref[#1]{Section~\ref*{#1}}}
\newcommand{\parbreak}{\ \\
\noindent}
\newcommand{\brieffiglink}[1]{\hyperref[#1]{Fig.~\ref*{#1}}}
\newcommand{\brieffigsublink}[2]{\hyperref[#1]{Fig.~\ref*{#1}#2}}

\newcommand{\vulgaronehalf}{${}^1\!\!\mskip0.3\thinmuskip/\!{}_2$}

\title{Practical Measurement of Voltage-Controlled Current Source Output Impedance for Applications in Transcranial Electrical Stimulation}

\author{\IEEEauthorblockN{Charl Linssen}
\IEEEauthorblockA{\textit{Donders Institute for Brain, Cognition and Behaviour} \\
\textit{Radboud University Nijmegen} \\
Nijmegen, The Netherlands\\
c.linssen@donders.ru.nl}
\and
\IEEEauthorblockN{Pieter Harpe}
\IEEEauthorblockA{\textit{Integrated Circuits Group} \\
\textit{Eindhoven University of Technology}\\
Eindhoven, The Netherlands \\
p.j.a.harpe@tue.nl}\\
\ \\
2021 IEEE Biomedical Circuits and Systems Conference (BioCAS)\\
October 6--9, 2021
}

%%%%%%%%%%%%%%%%%%%%%%%%%%%%%%%%%%%%%%%%%%%%%%%%%%%%%%%%%%%%%%%%%%%%%%%%%%%%%%
%%%%%%%%%%%%%%%%%%%%%%%%%%%%%%%%%%%%%%%%%%%%%%%%%%%%%%%%%%%%%%%%%%%%%%%%%%%%%%
\begin{document}

\maketitle

%%%%%%%%%%%%%%%%%%%%%%%%%%%%%%%%%%%%%%%%%%%%%%%%%%%%%%%%%%%%%%%%%%%%%%%%%%%%%%
%%%%%%%%%%%%%%%%%%%%%%%%%%%%%%%%%%%%%%%%%%%%%%%%%%%%%%%%%%%%%%%%%%%%%%%%%%%%%%
\begin{abstract}
\noindent A voltage-controlled current source (VCCS) is a key component in the electrical stimulation of neuronal tissue. We present a method for the evaluation of output impedance across frequency, of VCCS circuits with applications in transcranial electrical stimulation (tES). Two VCCS circuit architectures, one with a single-ended, and one with a differential output, are theoretically analysed and simulated, and the method is validated by matching these results with empirical measurements. Monte Carlo simulation of the measurement method itself is used to predict its range of applicability under real-world conditions. Both circuits, as well as the method used to determine output impedance, are easy to reproduce, using generic hardware components at low cost. The method described has immediate practical application value in neuroscience research, where it can be used in the deployment and further development of VCCS circuit architectures.
\end{abstract}

%%%%%%%%%%%%%%%%%%%%%%%%%%%%%%%%%%%%%%%%%%%%%%%%%%%%%%%%%%%%%%%%%%%%%%%%%%%%%%
%%%%%%%%%%%%%%%%%%%%%%%%%%%%%%%%%%%%%%%%%%%%%%%%%%%%%%%%%%%%%%%%%%%%%%%%%%%%%%
\begin{IEEEkeywords}
neuromodulation, neural, transcranial, current source
\end{IEEEkeywords}

%%%%%%%%%%%%%%%%%%%%%%%%%%%%%%%%%%%%%%%%%%%%%%%%%%%%%%%%%%%%%%%%%%%%%%%%%%%%%%
\section{Motivation}
\label{sec:motivation}
%%%%%%%%%%%%%%%%%%%%%%%%%%%%%%%%%%%%%%%%%%%%%%%%%%%%%%%%%%%%%%%%%%%%%%%%%%%%%%

Transcranial electrical stimulation (tES) is a relatively non-invasive way of altering the excitability of the brain. A direct, alternating or noise current (tDCS, tACS or tRNS, respectively) is delivered between two electrodes that have been placed into conductive contact with the subject's skin, on or near the scalp (\brieffiglink{fig:situation_sketch}, top). Bandwidth of the stimulation is typically below $1~\kilo\hertz$ and currents are below $2~\milli\ampere$ \cite{pmid26652115}\cite{pmid19109497}.

\begin{figure}[bt]
	\begin{subfigure}{\textwidth}
        
\hspace{-4.8cm}\makebox[\textwidth][c]{%
		
        }
        \caption*{}
        \label{fig:situation_sketch1}
    \end{subfigure}

	\begin{subfigure}{\textwidth}

\hspace{-4.5cm}\makebox[\textwidth][c]{%
\include{circuitikz_situation_sketch.tex}
}
        \caption*{\small}
        \label{fig:situation_sketch2}
    \end{subfigure}
\caption{\small Situation sketch (top panel) and equivalent circuit (bottom panel). In a typical tES session, the device is adjusted to supply a given current $I_L$ into a load $Z_L$ via two electrodes, each with interfacial impedance $Z_{elec}$. We assume the device is battery powered or in any case galvanically isolated; the ground node is thus elided in the bottom panel.}
\label{fig:situation_sketch}
\end{figure}

There is a trend towards smaller electrodes in tES, which allow for controlling the stimulation at a higher spatial resolution \cite{pmid23031743}. Smaller electrodes have a higher electrode (electrode/electrolyte, or interfacial) impedance (\brieffiglink{fig:situation_sketch}, bottom), and thus in general need higher drive voltages to maintain the same current. Drive voltages can also be paradoxically high, even with common tES electrode sizes (on the order of $50~\centi\meter^2$), for especially \emph{low} currents. For tDCS at $2.5~\milli\ampere$, an extrapolated voltage swing of at least $18.3~\volt$ is required from the VCCS, ``for the top 99th percentile'' of subjects \cite{pmid25018056}; \cite{pmid20488204} report using values as high as $66.7~\volt$.

To obtain larger output voltage swing, a VCCS with a differential output can be used. In a single-ended architecture, one of the electrodes is connected to ground, while the other is driven by the VCCS. In a differential design, instead, both sides are actively driven by the VCCS. This requires twice as many amplifiers or output drivers, but results in an effective doubling of the output voltage range when one side of the load is driven in antiphase with the other. Further benefits include an improved signal bandwidth, immunity to changes in the load, and noise immunity \cite{pmid24880419}.

Here, we present a universal, low-cost method to measure VCCS output impedance, to guide the design and empirical performance validation of any single-ended or differential output current source, in the operating regime that is typical for tES with human subjects. To improve the interpretability of obtained results, we selected two related circuits for evaluation, so that results may be compared on a relative basis. Each of these circuits is a variant of the well-known ``improved Howland'' current source, which can be built using commodity, off-the-shelf parts with low total cost, excellent performance, and large output voltage swing \cite{Franco1988}. Howland sources require precise matching of resistor values to obtain good performance, which can be adequately addressed by trimming using a single potentiometer (or two in the case of the differential source). These features make them an excellent alternative to custom silicon where access to tooling, turnaround time, customisation or cost are of concern.

We begin with a mathematical analysis (\briefseclink{sec:analysis}) and simulation studies (\briefseclink{sec:sim_results}), continue with empirical measurements (\briefseclink{sec:empirical-results}), and conclude in \briefseclink{sec:conclusion}.

\raggedbottom

%%%%%%%%%%%%%%%%%%%%%%%%%%%%%%%%%%%%%%%%%%%%%%%%%%%%%%%%%%%%%%%%%%%%%%%%%%%%%%
\section{Analysis}
\label{sec:analysis}
%%%%%%%%%%%%%%%%%%%%%%%%%%%%%%%%%%%%%%%%%%%%%%%%%%%%%%%%%%%%%%%%%%%%%%%%%%%%%%

%%%%%%%%%%%%%%%%%%%%%%%%%%%%%%%%%%%%%%%%%%%%%%%%%%%%%%%%%%%%%%%%%%%%%%%%%%%%%%
\subsection{Single-ended ``improved'' Howland VCCS}
\label{sec:single_ended_howland}

The improved Howland circuit is based on a standard op-amp and five precision resistors. It is a single-ended circuit, meaning one side of the load is connected to ground (\brieffiglink{fig:single_ended_howland}). The operation of the circuit can be understood as follows: there is both negative feedback (via $R_2$) and positive feedback (via $R_{4a}$). The difference between positive and negative feedback is proportional to the load current (via the ratio $R_2/R_{4b}$). No current flows into the input terminals of the op-amp, so the same difference in current exists between $R_1$ and $R_3$. But as $V_{pos}=V_{neg}$ in normal operation, these currents are in turn proportional to the input voltage $V_{in,pos}-V_{in,neg}$. Thus, overall, the load current is proportional to the input voltage.

%%%%%%%%%%%%%%%%%%%%%%%%%%%%%%%%%%%%%%%%%%%%%%%%%%%%%%%%%%%%%%%%%%%%%%%%%%%%%%
\subsubsection{DC analysis}

If we assume the op-amp to be ideal, the transfer function of the VCCS can be obtained based on application of Kirchoff's laws. Under the conditions that:
\begin{subequations}
\label{eq:single_ended_howland_conditions}
\begin{align}
R_1 &= R_3\\
R_2 &= R_{4a} + R_{4b}
\end{align}
\end{subequations}
the output current does not depend on output voltage (i.e. the $V_L$-dependent term vanishes). If the overall (differential) input voltage is written as $V_{in,dif\!f}=V_{in,pos}-V_{in,neg}$, then the transfer function is given by:
\begin{equation}
\label{eq:single_ended_gain}
I_L = g_mV_{in,dif\!f}
\end{equation}
with $g_m = R_2/(R_3R_{4b})$ the transconductance of the VCCS in units of Amp\`{e}re per Volt.

%%%%%%%%%%%%%%%%%%%%%%%%%%%%%%%%%%%%%%%%%%%%%%%%%%%%%%%%%%%%%%%%%%%%%%%%%%%%%%
\subsubsection{Compliance voltage}
\label{sec:single_ended_compliance_voltage}

The compliance voltage (maximum output voltage span) is in practice limited by the saturation voltage of the op-amp $V_{sat,pp}$ (e.g. $28~\volt$ for a $\pm15~\volt$ op-amp), and the voltage drop across the series resistor $R_{4b}$ caused by $I_L$, while the contribution of the positive feedback path (through $R_{4a}$) is negligible:

\begin{align}
\label{eq:single_ended_compliance_voltage}
|V_L|\leq V_{sat,pp} - R_{4b}|I_{L,max}|
\end{align}

\begin{figure}[t]
\hspace{-4.9cm}\makebox[\textwidth][c]{%
\scalebox{.75}{%
\include{circuitikz_single_ended_howland.tex}
}}
\caption{\small Circuit diagram of the single-ended ``improved'' Howland source. $Z_L$ is the load impedance external to the VCCS.}
\label{fig:single_ended_howland}
\end{figure}

\begin{figure}[tb]
\vspace{-1.5cm}\hspace{-4.6cm}\makebox[\textwidth][c]{%
\scalebox{.75}{%
\include{circuitikz_differential_howland.tex}
}}
\caption{\small Circuit diagram of the fully differental ``improved'' Howland source. $Z_L$ is the load impedance external to the VCCS.}
\label{fig:differential_howland}
\end{figure}

%%%%%%%%%%%%%%%%%%%%%%%%%%%%%%%%%%%%%%%%%%%%%%%%%%%%%%%%%%%%%%%%%%%%%%%%%%%%%%%
%%%%%%%%%%%%%%%%%%%%%%%%%%%%%%%%%%%%%%%%%%%%%%%%%%%%%%%%%%%%%%%%%%%%%%%%%%%%%%%
\subsection{Differential version of the ``improved'' Howland VCCS}
\label{sec:differential_howland}

The differential version that we study here uses two op-amps and six precision resistors (\brieffiglink{fig:differential_howland}) \cite{simmonds2009differential}. It operates in a manner analogous to the single-ended version. Each op-amp balances positive and negative feedback, the difference between the two being determined by the voltage drop across resistors $R_{2b}$ and $R_{4b}$ that are in series with the load.

%%%%%%%%%%%%%%%%%%%%%%%%%%%%%%%%%%%%%%%%%%%%%%%%%%%%%%%%%%%%%%%%%%%%%%%%%%%%%%%
\subsubsection{DC analysis}

Again we assume an ideal op-amp, and derive the transfer function by applying Kirchoff's laws. Under the conditions that $V_{in,pos} = -V_{in,neg}$ and
\begin{subequations}
\label{eq:diff_howland_conditions}
\begin{align}
R_{2a} &= R_{4a}\\
R_{2b} &= R_{4b}\\
R_1 = R_3 &= R_{2a} + R_{2b}
\end{align}
\end{subequations}
the output current does not depend on output voltage (i.e. the $V_L$ term vanishes). The transfer function can then be written as:
\begin{equation}
\label{eq:diff_gain}
I_L = g_m V_{in,dif\!f}
\end{equation}
with $g_m = 1/R_{2b}$.

%%%%%%%%%%%%%%%%%%%%%%%%%%%%%%%%%%%%%%%%%%%%%%%%%%%%%%%%%%%%%%%%%%%%%%%%%%%%%%%
\subsubsection{Compliance voltage}

The main limiting factor of the compliance voltage is, as before, the saturation voltage of the op-amp, and secondly, the voltage drop across (in this case not one but two) resistors $R_{2b}$ and $R_{4b}$ (with $R_{2b}=R_{4b}$). If resistor values are chosen to be equal (see \tablelink{tbl:resistor_vales}), this yields a compliance voltage twice that of the single-ended variant:
\begin{align}
\label{eq:diff_compliance_voltage}
|V_L|\leq 2\left(V_{sat,pp} - R_{2b}|I_{L,max}|\right)
\end{align}

%%%%%%%%%%%%%%%%%%%%%%%%%%%%%%%%%%%%%%%%%%%%%%%%%%%%%%%%%%%%%%%%%%%%%%%%%%%%%%%
%%%%%%%%%%%%%%%%%%%%%%%%%%%%%%%%%%%%%%%%%%%%%%%%%%%%%%%%%%%%%%%%%%%%%%%%%%%%%%%
\section{Simulation results}
\label{sec:sim_results}

%%%%%%%%%%%%%%%%%%%%%%%%%%%%%%%%%%%%%%%%%%%%%%%%%%%%%%%%%%%%%%%%%%%%%%%%%%%%%%%
\subsection{Monte Carlo simulation of DC output resistance}
\label{sec:monte_carlo}
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

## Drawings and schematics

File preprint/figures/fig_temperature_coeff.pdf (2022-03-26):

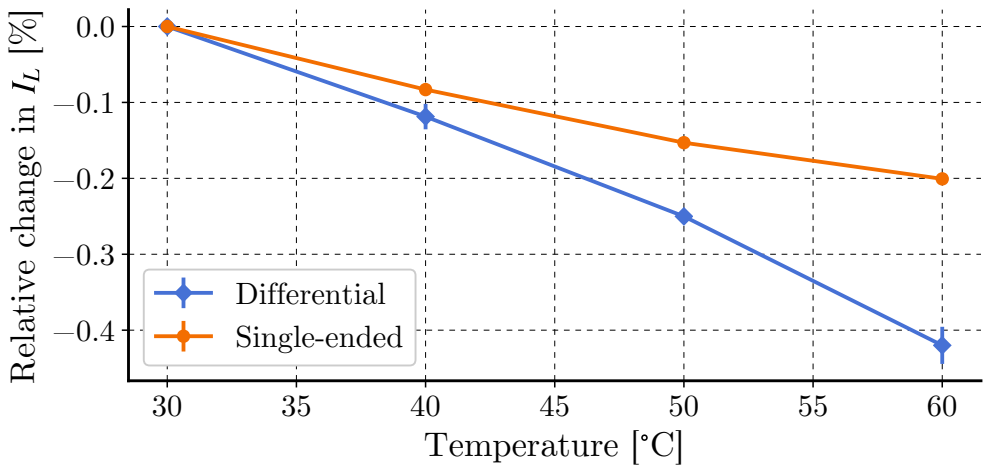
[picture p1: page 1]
60 Temperature [ C]; Differential Single-ended

Relative change in IL [%]

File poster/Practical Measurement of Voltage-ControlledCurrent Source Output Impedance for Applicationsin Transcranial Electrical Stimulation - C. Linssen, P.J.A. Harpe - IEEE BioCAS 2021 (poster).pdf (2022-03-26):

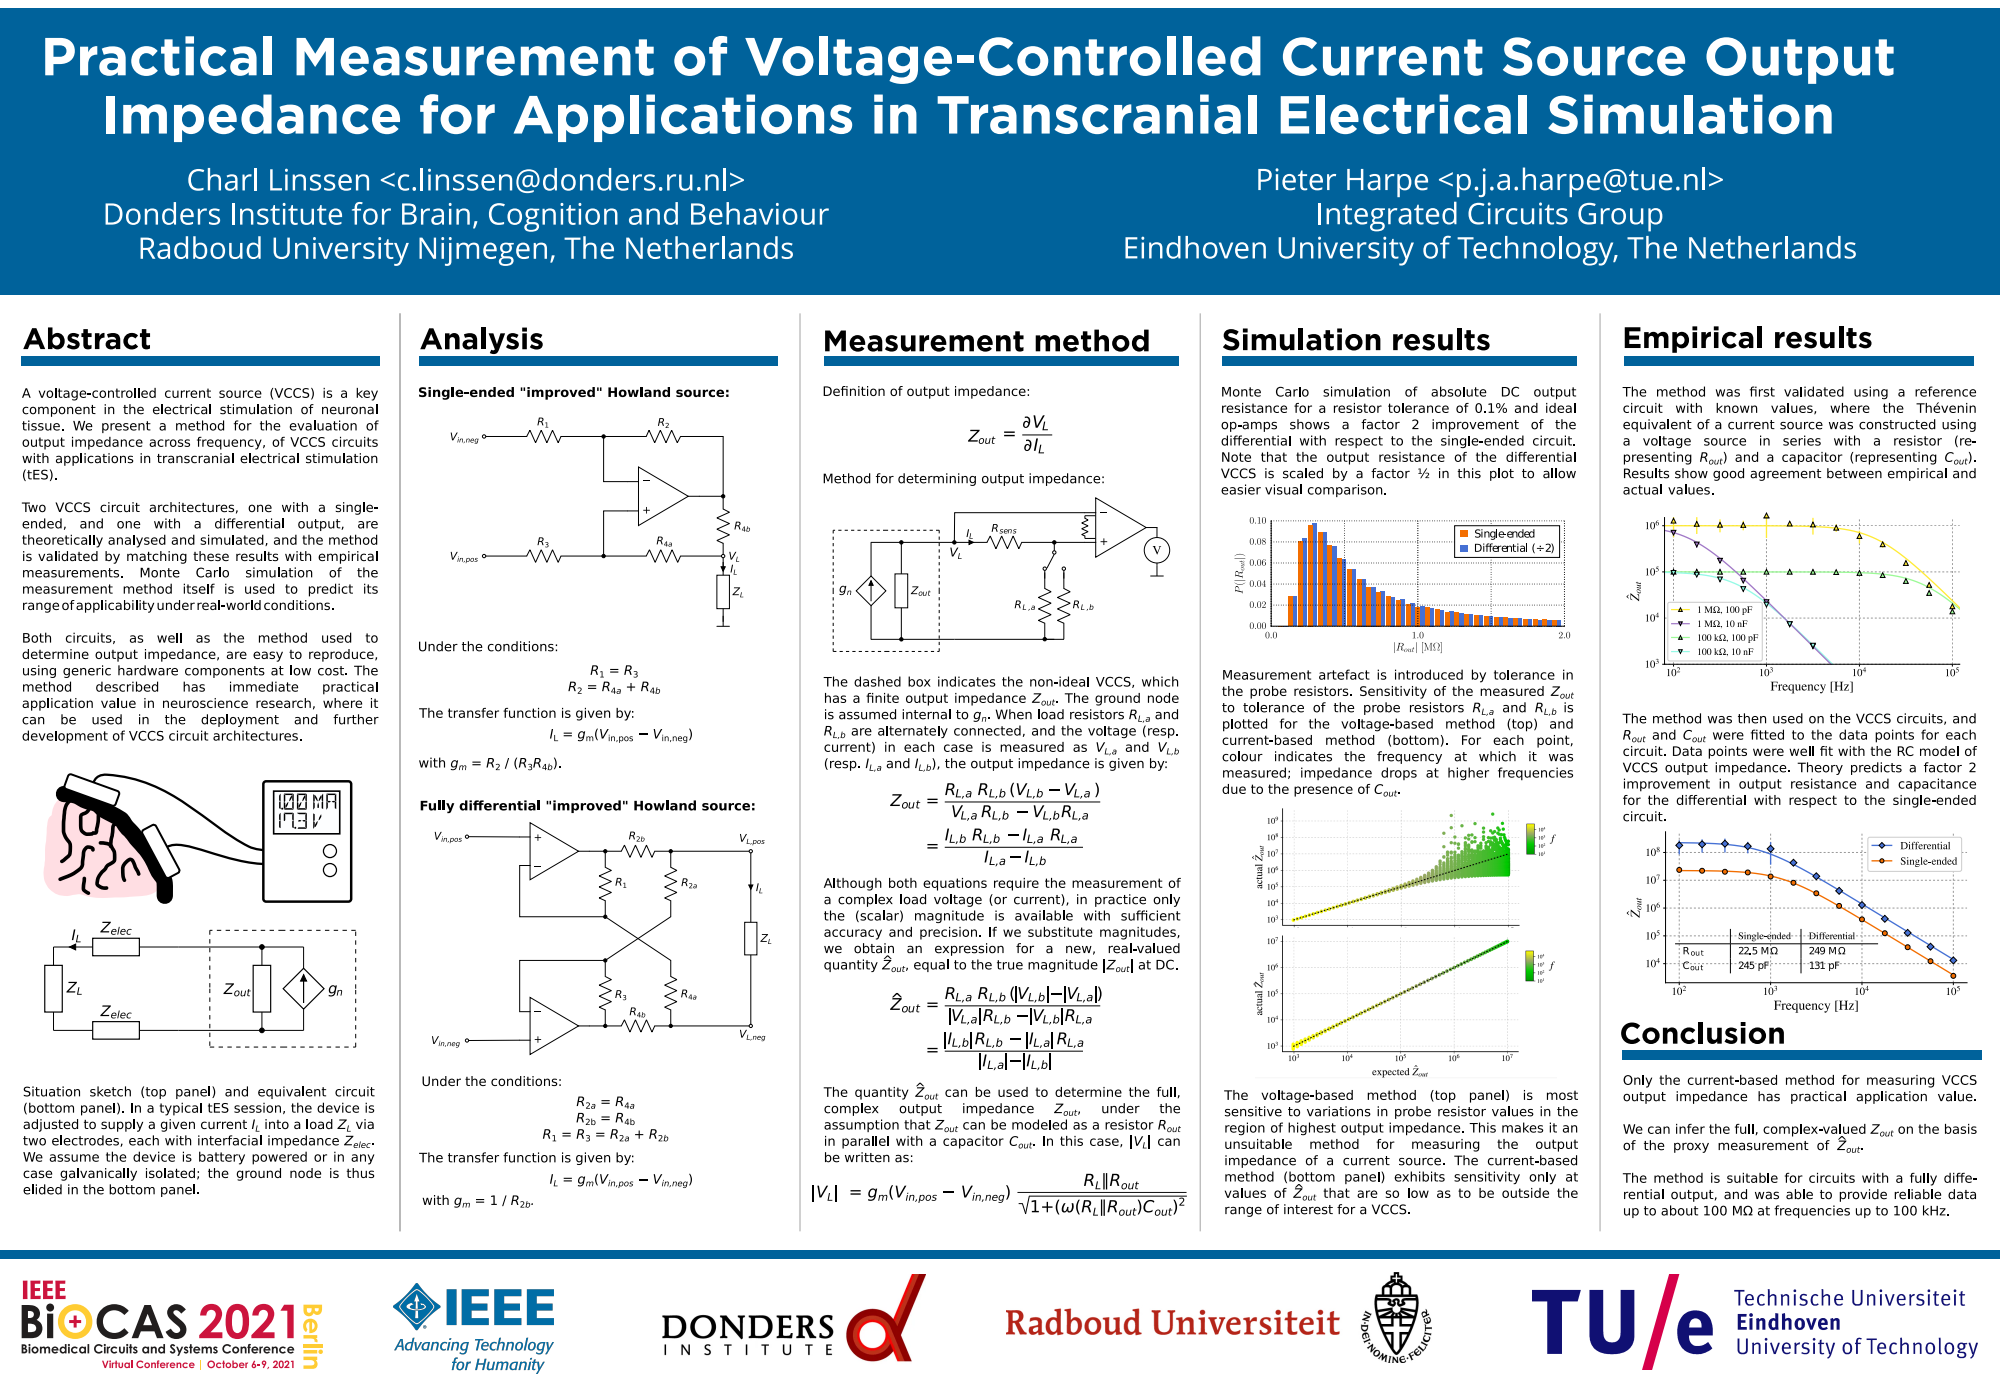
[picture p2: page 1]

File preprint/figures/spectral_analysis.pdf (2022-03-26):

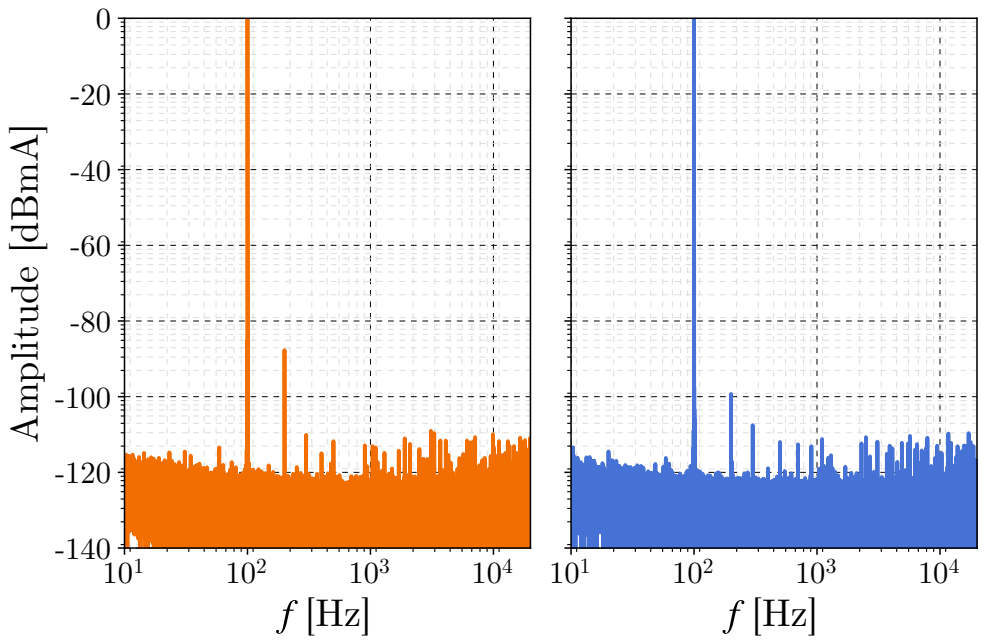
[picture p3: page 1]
Amplitude [dBmA]

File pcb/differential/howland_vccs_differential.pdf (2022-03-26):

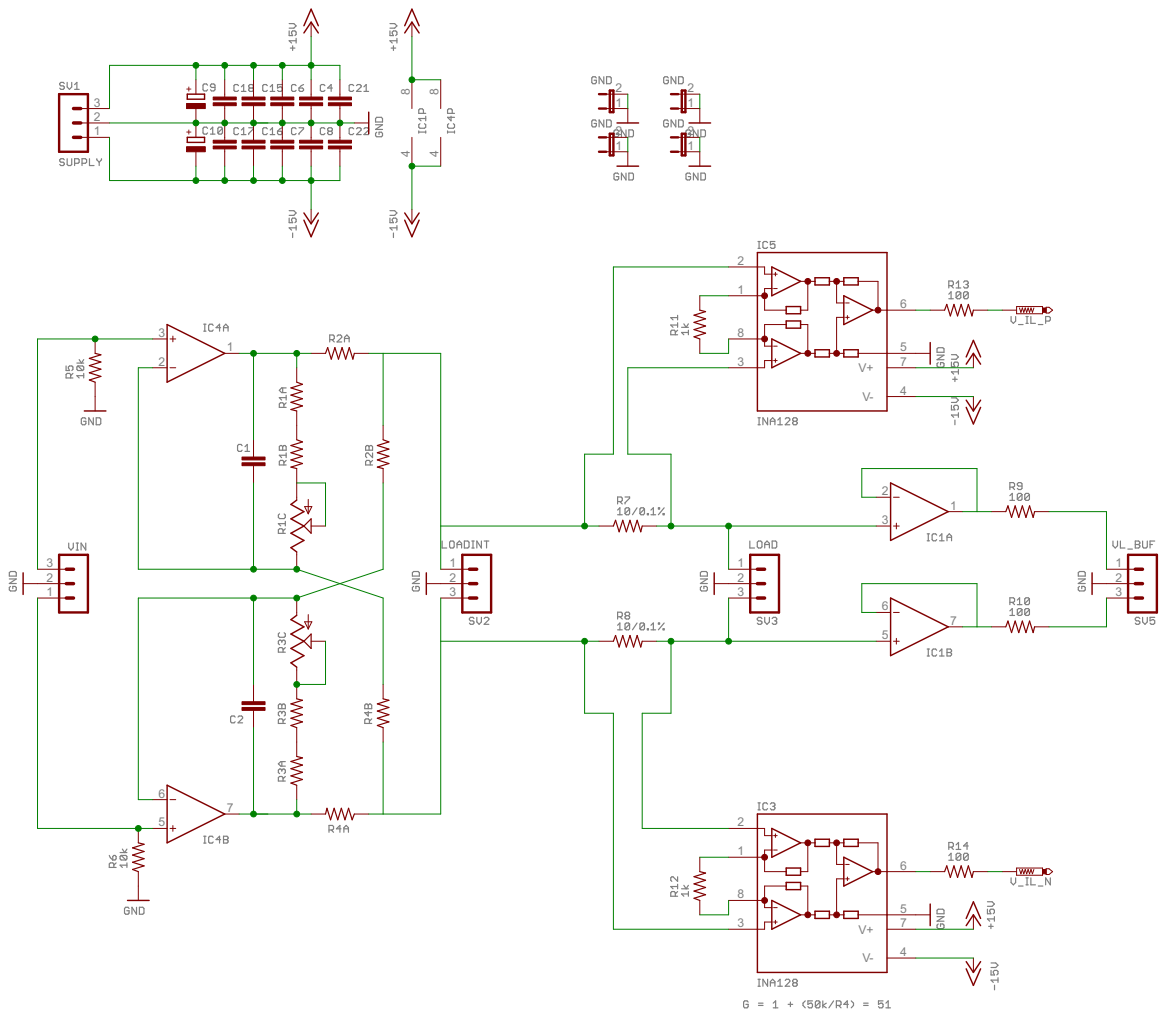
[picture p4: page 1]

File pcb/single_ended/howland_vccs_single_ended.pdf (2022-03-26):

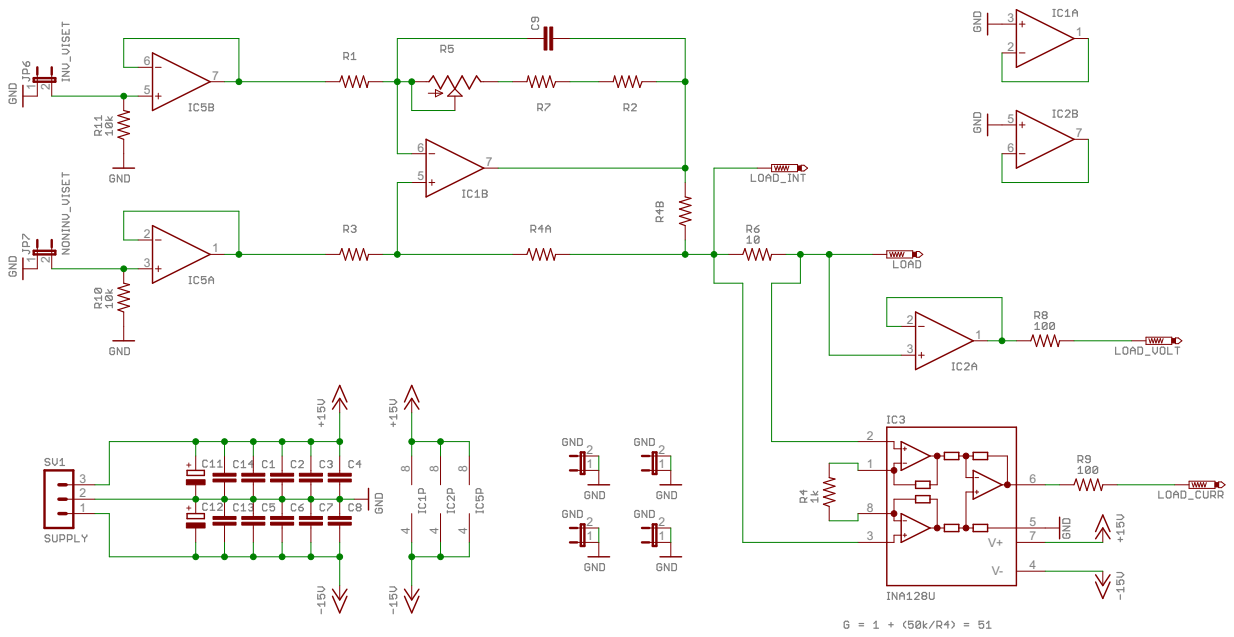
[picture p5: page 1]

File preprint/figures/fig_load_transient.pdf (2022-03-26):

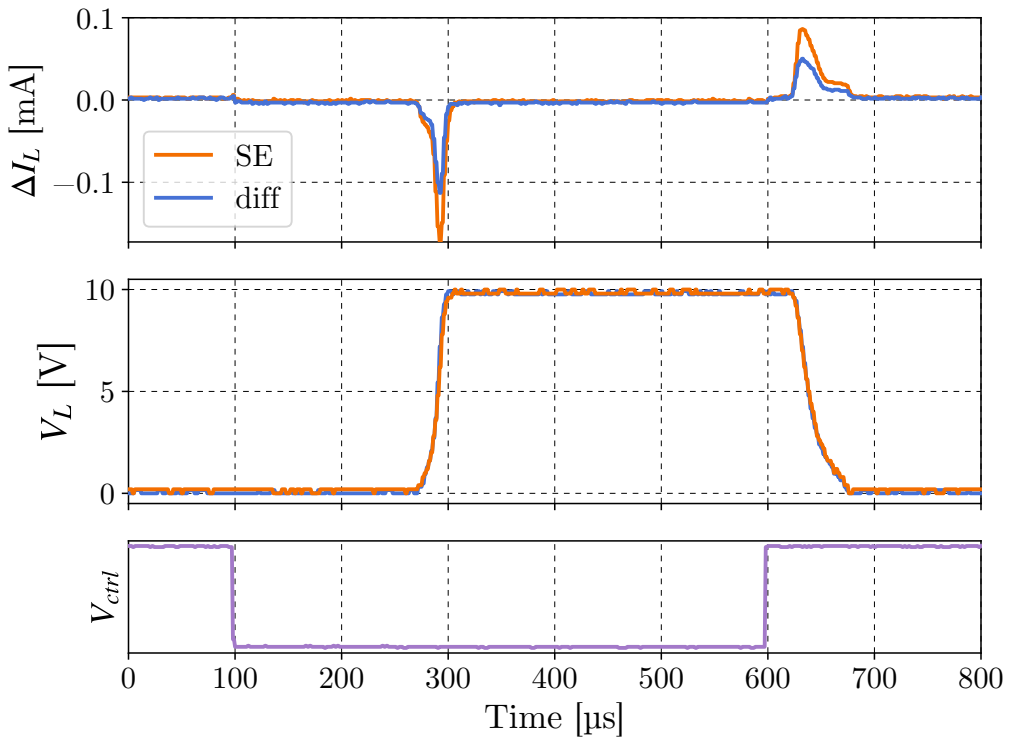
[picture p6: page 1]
Time [µs]; Vctrl

SE
diff

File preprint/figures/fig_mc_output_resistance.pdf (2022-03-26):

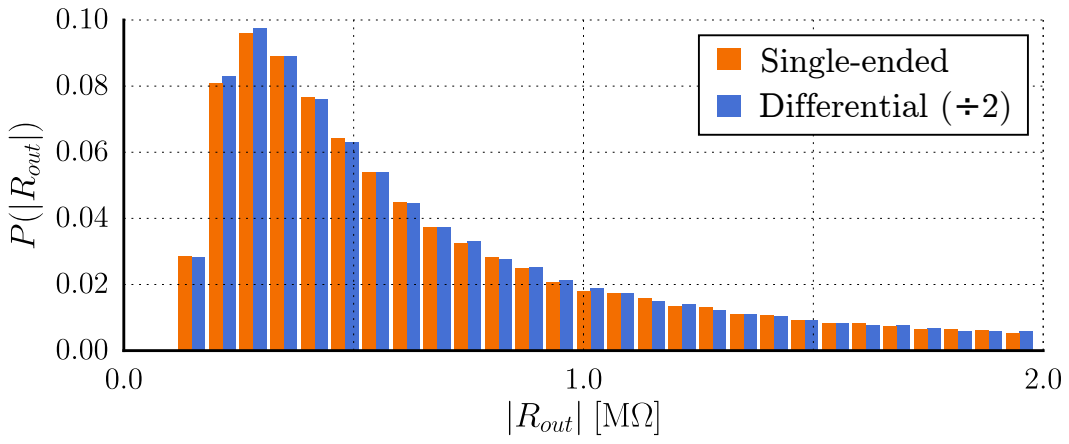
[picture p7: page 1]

Single-ended
Differential (÷2)

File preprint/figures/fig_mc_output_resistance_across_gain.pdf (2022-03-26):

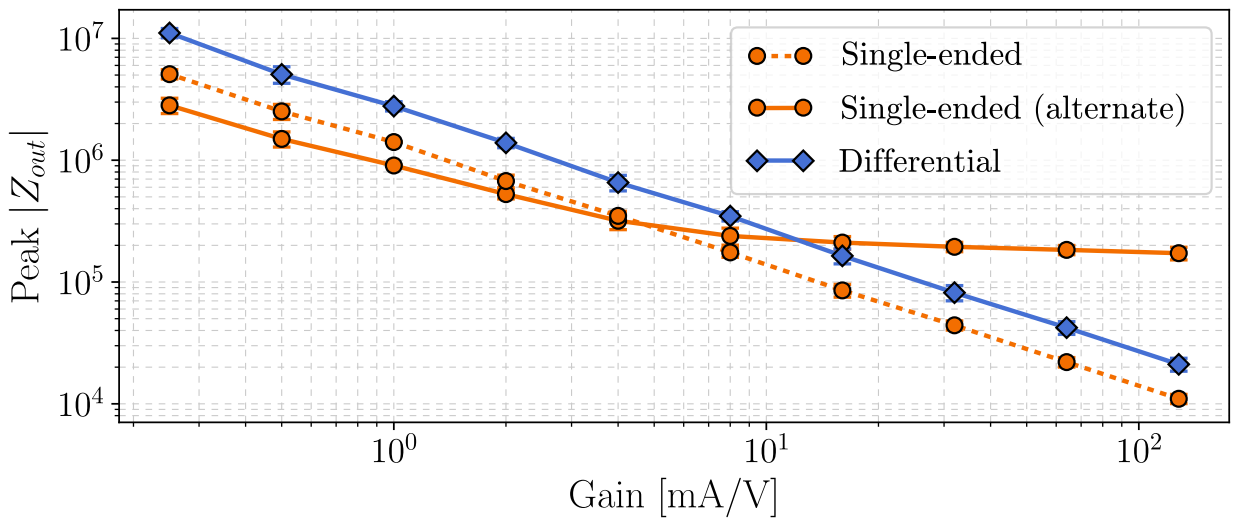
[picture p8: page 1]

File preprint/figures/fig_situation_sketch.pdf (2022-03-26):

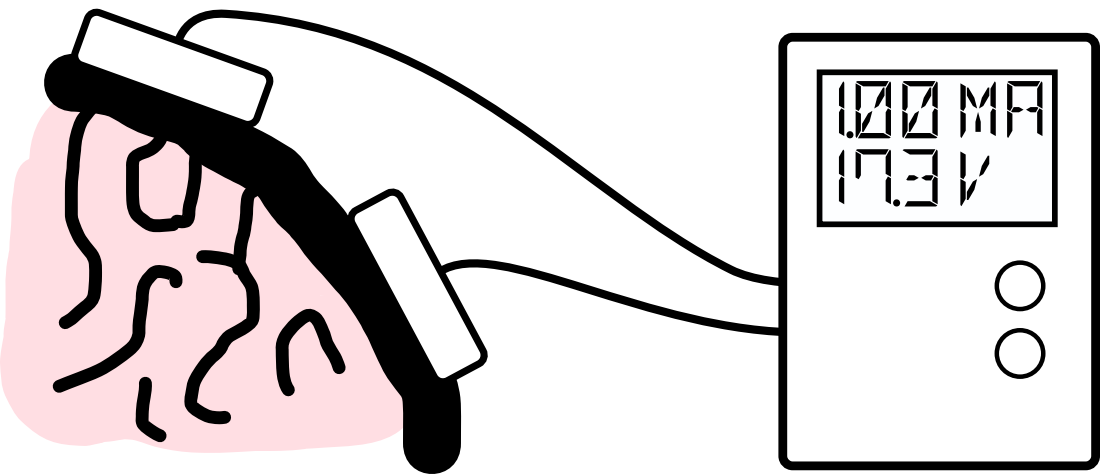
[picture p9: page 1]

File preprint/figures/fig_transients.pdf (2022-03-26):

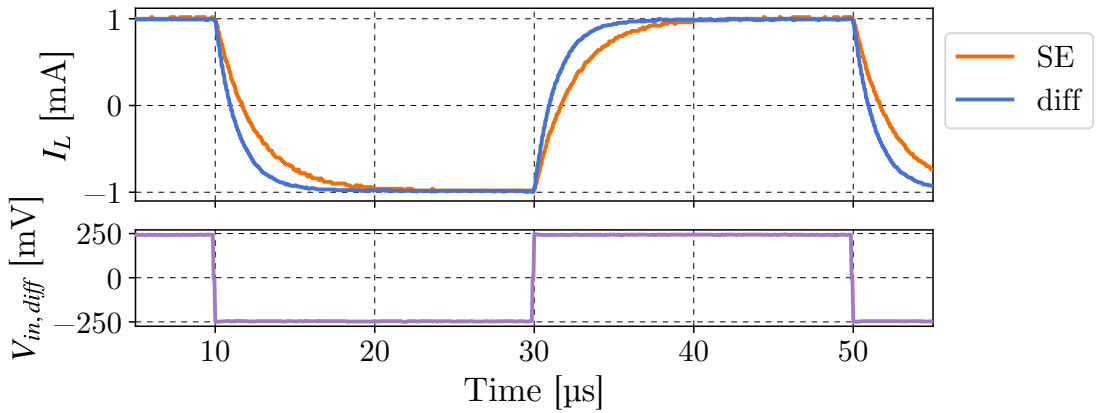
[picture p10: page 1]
SE diff; Time [µs]; Vin, diff [mV]

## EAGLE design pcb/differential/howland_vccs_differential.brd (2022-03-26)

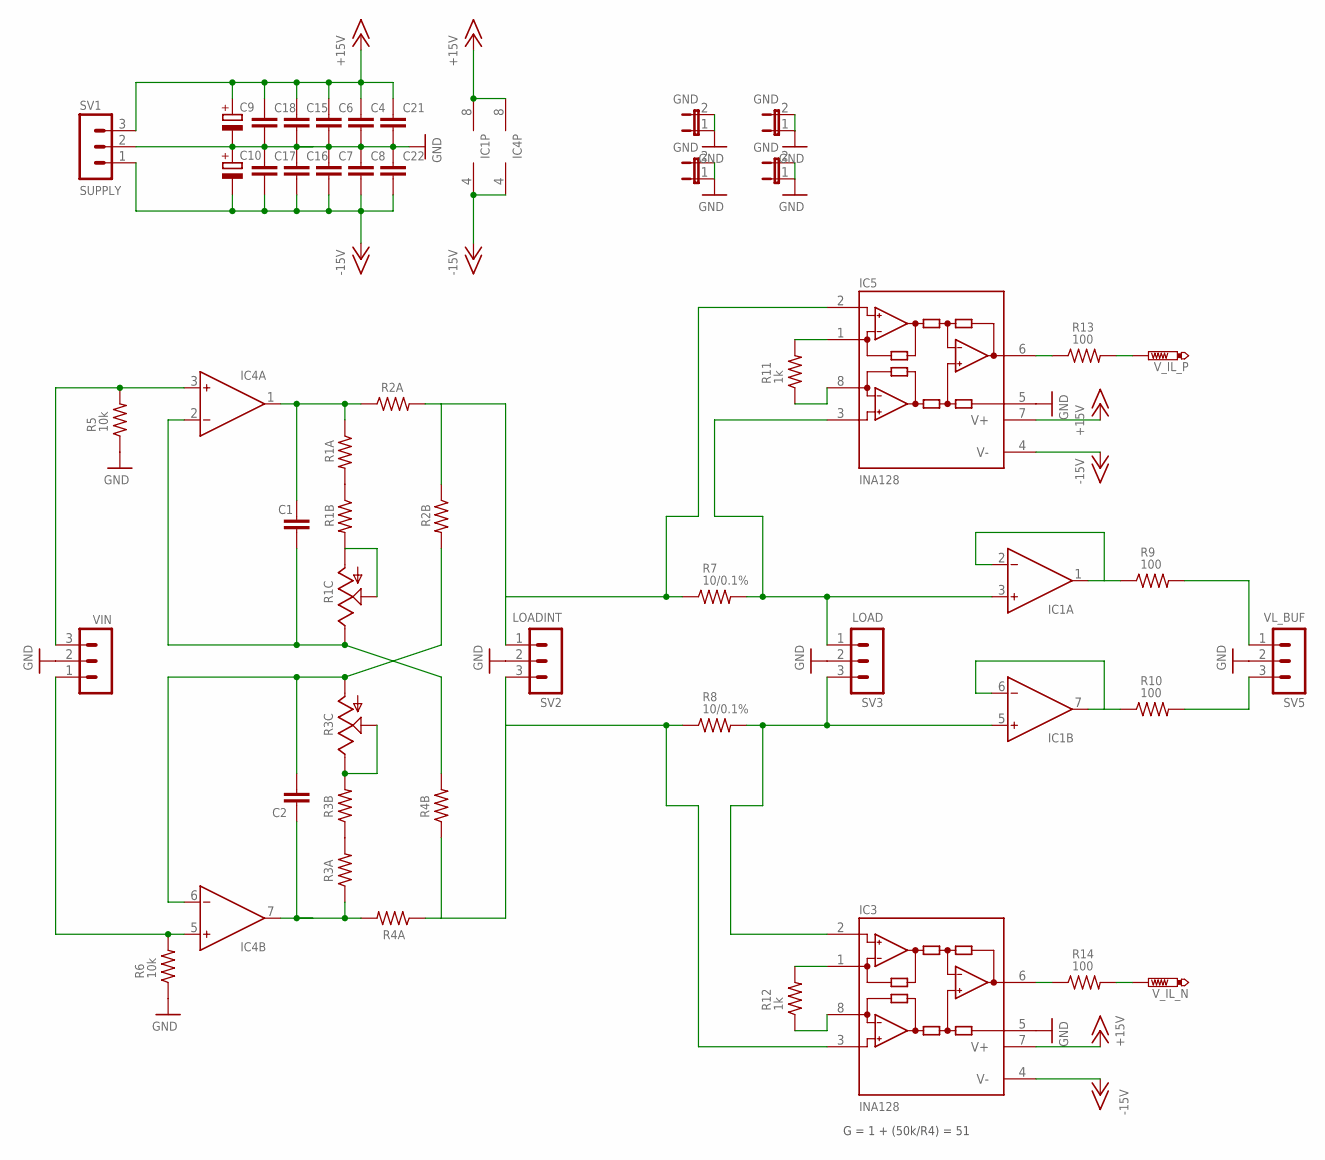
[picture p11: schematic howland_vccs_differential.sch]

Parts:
C1, C2, C4, C6, C7, C8, C15, C16, C17, C18, C21, C22: C-EUC1206; C1206
C9, C10: CPOL-EUC/6032-28R; C/6032-28R
IC1, IC4: OPA2192; SO8
IC3, IC5: INA128; SO08
JP8, JP10, JP11, JP12: GND; JP1
R1A, R1B, R2A, R2B, R3A, R3B, R4A, R4B: R-US_R1206; R1206
R1C, R3C: TRIM_US-3223J; 3223J
R5, R6: 10k; R1206
R7, R8: 10/0.1%; R1206
R9, R10, R13, R14: 100; R1206
R11, R12: 1k; R1206
SV1: SUPPLY; MA03-1
SV2: LOADINT; MA03-1
SV3: LOAD; MA03-1
SV5: VL_BUF; MA03-1
VIN: MA03-1
V_IL_N: PTR1PAD1-13; P1-13
V_IL_P: PTR1PAD1-13; P1-13

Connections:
+15V: C4.1, C6.1, C9.+, C15.1, C18.1, C21.1, IC1.8 (V+), IC3.7 (V+), IC4.8 (V+), IC5.7 (V+), SV1.3
-15V: C7.2, C8.2, C10.-, C16.2, C17.2, C22.2, IC1.4 (V-), IC3.4 (V-), IC4.4 (V-), IC5.4 (V-), SV1.1
GND: C4.2, C6.2, C7.1, C8.1, C9.-, C10.+, C15.2, C16.1, C17.1, C18.2, C21.2, C22.1, IC3.5 (REF), IC5.5 (REF), JP8.1, JP8.2, JP10.1, JP10.2, JP11.1, JP11.2, JP12.1, JP12.2, R5.1, R6.1, SV1.2, SV2.2, SV3.2, SV5.2, VIN.2
unnamed: IC5.2 (-IN), R2A.2, R2B.1, R7.1, SV2.1
unnamed: C1.2, IC4.2 (IN-), R1C.3 (E), R4B.2
unnamed: C1.1, IC4.1 (OUT), R1A.1, R2A.1
unnamed: IC1.6 (IN-), IC1.7 (OUT), R10.1
unnamed: R1B.2, R1C.1 (A), R1C.2 (S)
unnamed: IC3.1 (RG), R12.2
unnamed: IC3.8 (RG), R12.1
unnamed: IC3.6 (OUT), R14.1
unnamed: R1A.2, R1B.1
unnamed: IC1.1 (OUT), IC1.2 (IN-), R9.1
unnamed: IC4.5 (IN+), R6.2, VIN.1
unnamed: IC4.3 (IN+), R5.2, VIN.3
unnamed: R10.2, SV5.3
unnamed: R14.2, V_IL_N.TP
unnamed: R9.2, SV5.1
unnamed: C2.2, IC4.6 (IN-), R2B.2, R3C.1 (A)
unnamed: C2.1, IC4.7 (OUT), R3A.1, R4A.2
unnamed: R3B.2, R3C.2 (S), R3C.3 (E)
unnamed: IC5.1 (RG), R11.2
unnamed: IC5.8 (RG), R11.1
unnamed: IC5.6 (OUT), R13.1
unnamed: R13.2, V_IL_P.TP
unnamed: IC1.3 (IN+), IC5.3 (+IN), R7.2, SV3.1
unnamed: R3A.2, R3B.1
unnamed: IC3.3 (+IN), R4A.1, R4B.1, R8.1, SV2.3
unnamed: IC1.5 (IN+), IC3.2 (-IN), R8.2, SV3.3

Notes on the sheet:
G = 1 + (50k/R4) = 51

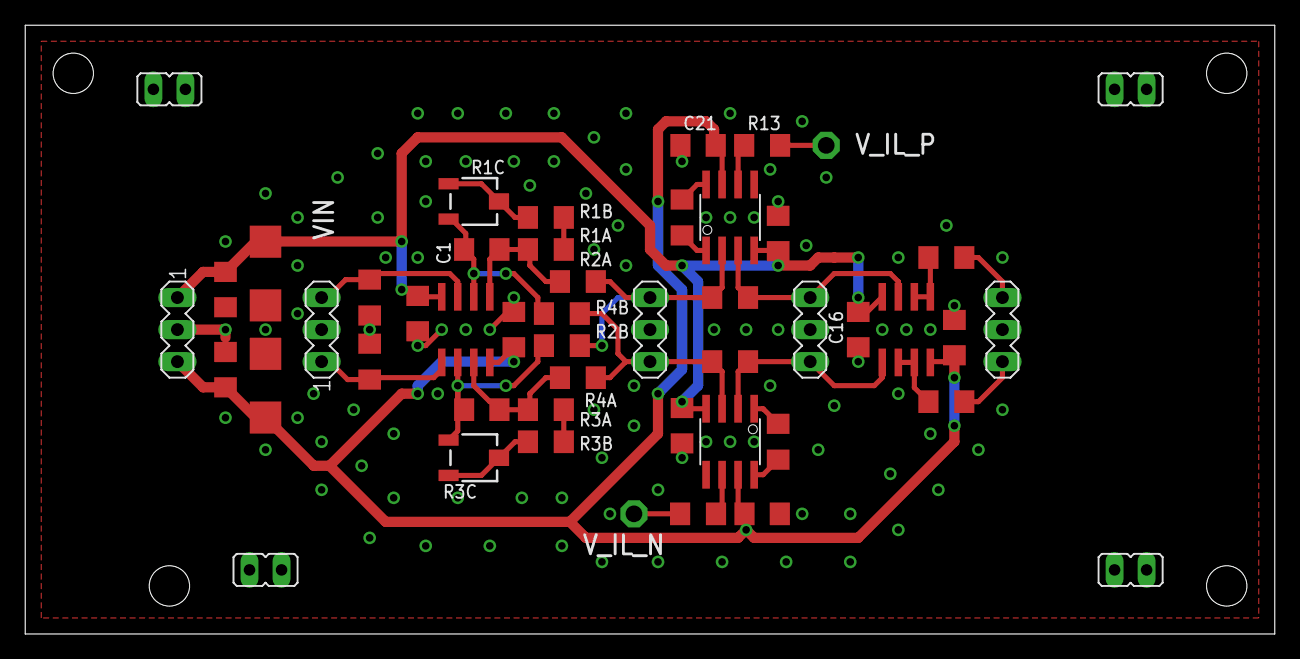
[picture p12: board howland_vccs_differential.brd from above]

Board: 2 copper layers, 99.1 x 48.3 mm, 49 parts (0 on the bottom side), 29 nets.

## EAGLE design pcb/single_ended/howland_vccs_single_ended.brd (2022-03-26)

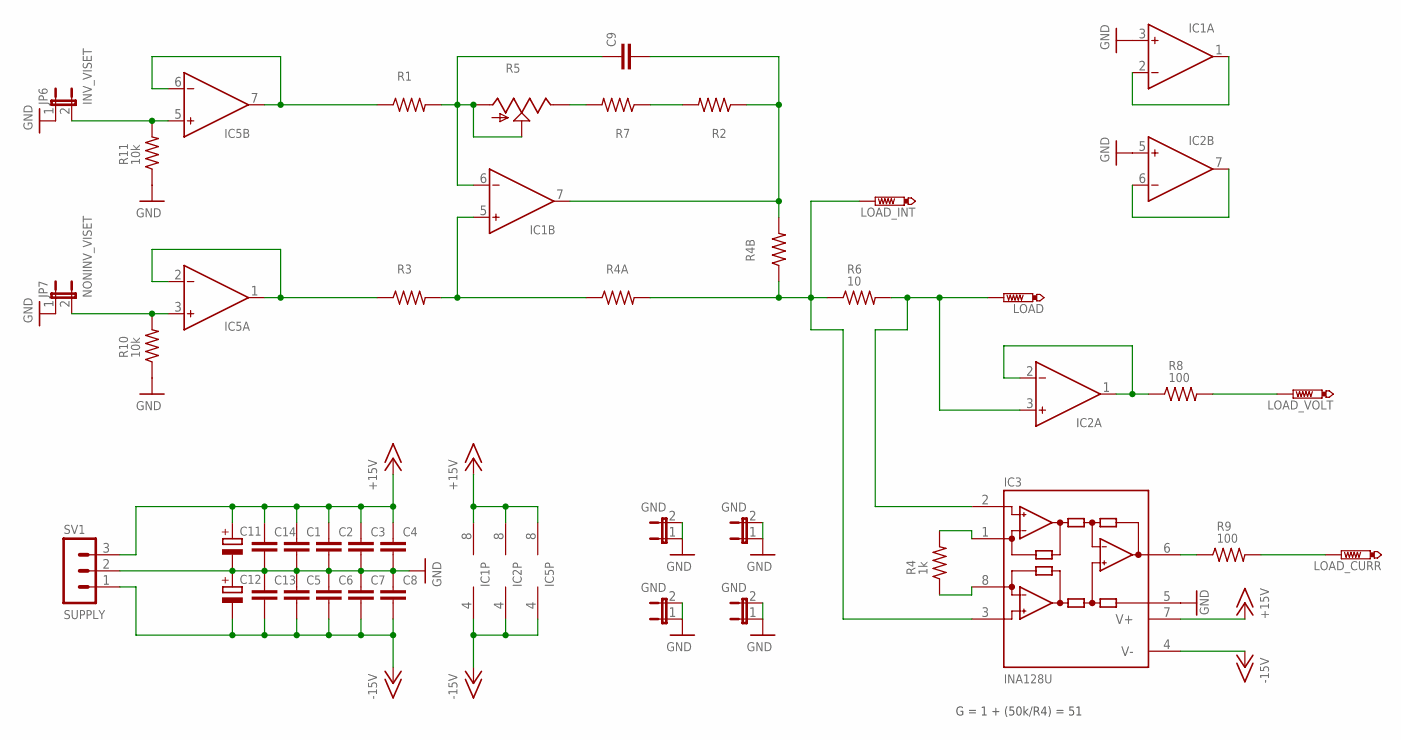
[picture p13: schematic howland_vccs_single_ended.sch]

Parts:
C1, C2, C3, C4, C5, C6, C7, C8, C9, C13, C14: C-EUC1206; C1206
C11, C12: CPOL-EUC/6032-28R; C/6032-28R
IC1, IC2: LM358; SO8
IC3: INA128U; SO08
IC5: OPA2192; SO8
JP4, JP8, JP9, JP10: GND; JP1
JP6: INV_VISET; JP1
JP7: NONINV_VISET; JP1
LOAD: PTR1PAD1-13; P1-13
LOAD_CURR: PTR1PAD1-13; P1-13
LOAD_INT: PTR1PAD1-13; P1-13
LOAD_VOLT: PTR1PAD1-13; P1-13
R1, R3: 12.25k/0.1%; R1206
R2, R4A: 10k/.1%; R1206
R4: 1k; R1206
R4B: 250; R1206
R5: 100; 3223J
R6: 10; R1206
R7: 200; R1206
R8, R9: 100; R1206
R10, R11: 10k; R1206
SV1: SUPPLY; MA03-1

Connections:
+15V: C1.1, C2.1, C3.1, C4.1, C11.+, C14.1, IC1.8 (V+), IC2.8 (V+), IC3.7 (V+), IC5.8 (V+), SV1.3
-15V: C5.2, C6.2, C7.2, C8.2, C12.-, C13.2, IC1.4 (V-), IC2.4 (V-), IC3.4 (V-), IC5.4 (V-), SV1.1
GND: C1.2, C2.2, C3.2, C4.2, C5.1, C6.1, C7.1, C8.1, C11.-, C12.+, C13.1, C14.2, IC1.3 (IN+), IC2.5 (IN+), IC3.5 (REF), JP4.1, JP4.2, JP6.1, JP7.1, JP8.1, JP8.2, JP9.1, JP9.2, JP10.1, JP10.2, R10.1, R11.1, SV1.2
unnamed: IC2.1 (OUT), IC2.2 (IN-), R8.1
unnamed: IC1.5 (IN+), R3.2, R4A.1
unnamed: C9.1, IC1.6 (IN-), R1.2, R5.1 (A), R5.2 (S)
unnamed: C9.2, IC1.7 (OUT), R2.1, R4B.2
unnamed: IC3.3 (+IN), LOAD_INT.TP, R4A.2, R4B.1, R6.1
unnamed: R5.3 (E), R7.2
unnamed: IC3.1 (RG), R4.2
unnamed: IC3.8 (RG), R4.1
unnamed: IC3.6 (OUT), R9.1
unnamed: IC1.1 (OUT), IC1.2 (IN-)
unnamed: R2.2, R7.1
unnamed: IC5.1 (OUT), IC5.2 (IN-), R3.1
unnamed: IC5.6 (IN-), IC5.7 (OUT), R1.1
unnamed: IC5.3 (IN+), JP7.2, R10.2
unnamed: IC5.5 (IN+), JP6.2, R11.2
unnamed: LOAD_VOLT.TP, R8.2
unnamed: LOAD_CURR.TP, R9.2
unnamed: IC2.6 (IN-), IC2.7 (OUT)
unnamed: IC2.3 (IN+), IC3.2 (-IN), LOAD.TP, R6.2

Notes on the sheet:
G = 1 + (50k/R4) = 51

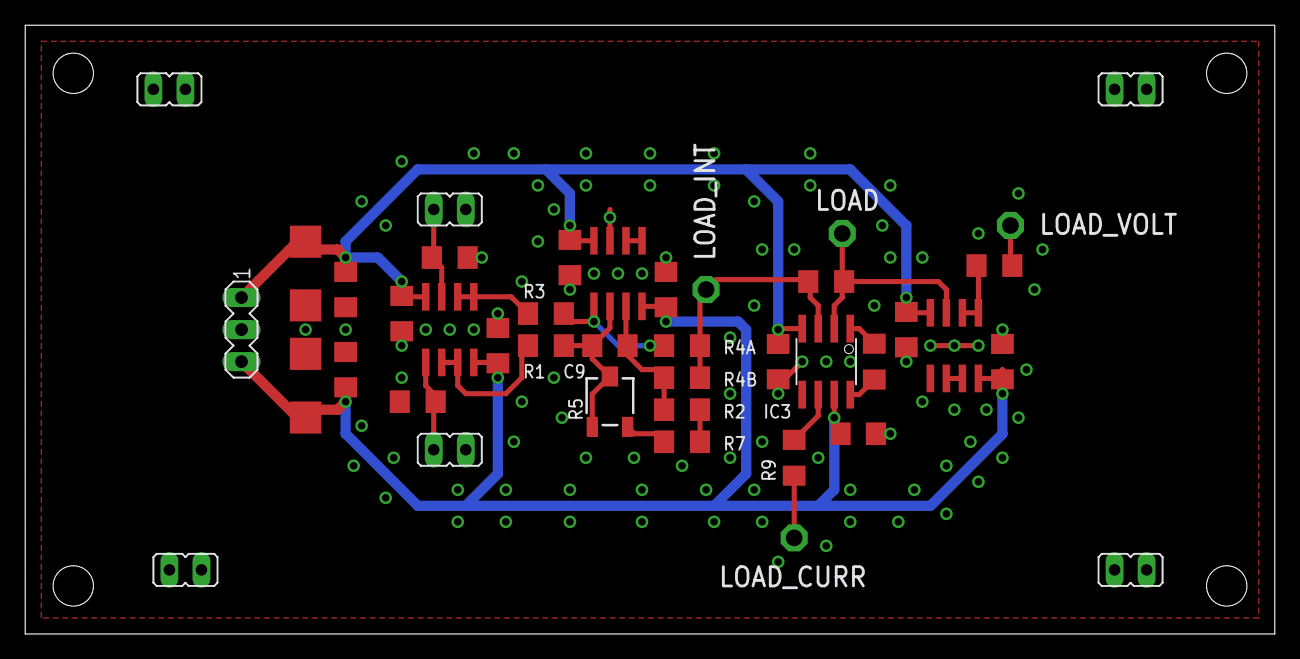
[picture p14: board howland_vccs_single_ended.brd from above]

Board: 2 copper layers, 99.1 x 48.3 mm, 41 parts (0 on the bottom side), 22 nets.
